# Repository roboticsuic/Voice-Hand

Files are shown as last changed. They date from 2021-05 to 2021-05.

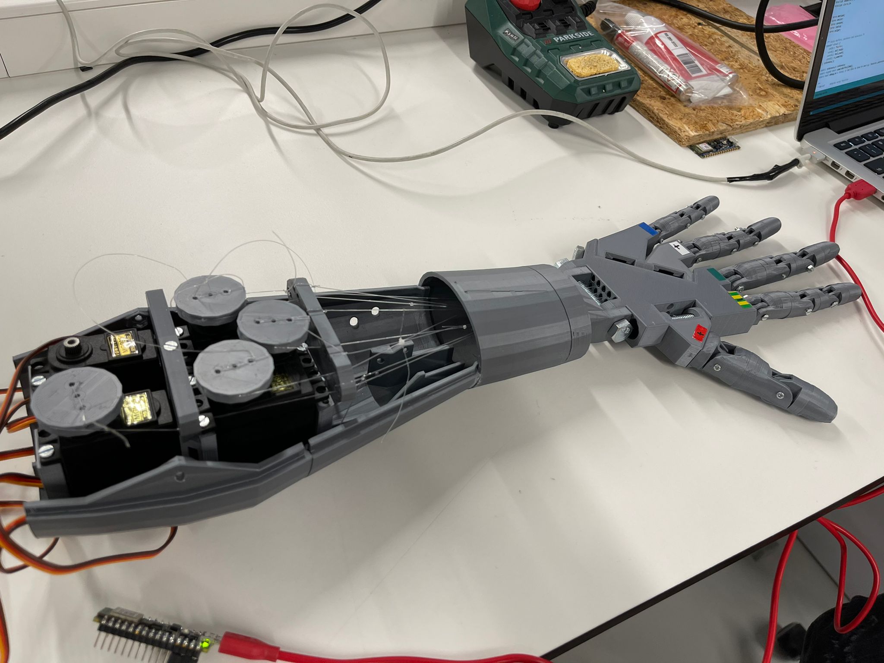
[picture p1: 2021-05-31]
Images and videos/120114522-ced4ec00-c17f-11eb-80c8-0a89fcd72188.jpg

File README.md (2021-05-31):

# Voice-Hand
<h3>A 3D-printed dynamic hand prosthesis with voice recognition software. 
  
Members: Cedric Cordova, Antonio Julia, Saioa Ortiz, and Eduardo Saman
<h2>
INTRODUCTION </h2>
<p>
Do you live with only one hand or ever feel that two just is not enough? The task of biomimicking the human hand, the most dextrous tool ever devised, has taken on new significance and nowadays, owing to new technologies, including 3D printing, it is possible to build your own prosthesis and in a very economical way. 

The project that has been carried out is based on the open-source 3D robotics work called InMoov and the proposed modifications of Patrick S. in its job: “DIY Prosthetic Hand & Forearm (Voice Controlled)”,  which can be found in instructables.com. In this way, this project aims to activate the movement of a prosthetic hand by means of the voice. To do so, it has been used an Arduino Nano 33 BLE Sense system and the software Edge Impulse (which utilizes machine learning and neural networks). The main interest of voice control remains in the fact that muscles are not required.

In relation to the movements that our prosthesis can perform, these can be classified as ROCK (closing all the fingers to form a fist with the hand) or TEST (contracting and relaxing one by one all the fingers). 

Therefore, this report compiles the materials that have been needed, the procedures that have been followed and the problems that have been encountered throughout the challenge, as well as possible improvements that could be made to optimize this prosthesis. Thos projet is based on:https://www.instructables.com/Voice-Controlled-Prosthetic-Hand-Forearm/
	
</p>



<h2> MATERIALS, SOFTWARES, and HARDWARE</h2>
<ul>
<li>Arduino Nano 33 BLE Sense(https://store.arduino.cc/arduino-nano-33-ble-sense)</li>
<li>5x Servo motors MG995(https://es.banggood.com/6X-MG995-High-Torque-Metal-Gear-Analog-Servo-for-RC-Airplane-Models-p-1181877.html?rmmds=detail-left-hotproducts&cur_warehouse=CZ)</li>
Screws:
<li>14 x 2.5mm (or 3mm) bolts (20mm long)</li>
<li>1 x 8mm bolt (55mm long)</li>
<li>1 x 8mm bolt (80mm long)</li>
<li>1 x 8mm bolt (60mm long)</li>
<li>Wires(Macho Macho)</li>
<li>Pins</li>
<li>Fishing line (Nylon)</li>
<li>Breadboard</li>
<li>PRUSA 3D printer</li>
<li>PLA(1.75mm fillament)</li>
<li>Sandpaper</li>
<li>Super glue</li>
<li>Greese</li>
<li>3D Printed(Print each file once)</li>
<li>Ultimaker Cura software</li>
<li>SOLIDWORKS software</li>
<li>Edge Impulse software</li>
</ul>
	
 <h3> Go to the repository for STL files of each part.
</h3>

<h4> 
	APPROXIMATE COST:69€
</h4>


<h2>METHODS</h2>
<p>1. First of all, you need to print out all the parts, which can be found on thingiverse.com. For this, the print setting we used for all the parts were:
</p>
<table>
<thead>
	<tr>
		PRINTING PARAMETERS
	</tr>
</thead>
<tbody>
	<tr>
		<td>Printing Temperature</td>
		<td>Optimal temperature for PLA is 200ºC</td>
	</tr>
	<tr>
		<td>Bed Temperature</td>
		<td>60ºC</td>
	</tr>
  	<tr>
		<td>Speed</td>
		<td>40 mm/s</td>
	</tr>
  	<tr>
		<td>Infill</td>
		<td>20%</td>
	</tr>
  	<tr>
		<td>Support</td>
		<td>None/Change of orientation</td>
	</tr>
</tbody>
</table>

<p>
This parameters may change if the printer used is different, the one we used was PRUSA 

The parts that were printed are the following (you can find them in the zipfile above):</p>
<ul>
	<li>Fingers: Auriculaire3.stl, Index3.stl, Majeure3.stl, ringfinger3.stl, thumb5.stl </li>
	<li> Wrist: robpart1V2.stl,robpart2V3, robpart3V3, WristsmallV3.stl, WristlargeV4.stl</li>
	<li> Half forearm: robpart2V4.stl, robpart3V4.stl, robpart4V3.stl, robpart5V3.stl</li>
	<li>Motor Mounts/Pieces: RobServoBedV5.stl, RobCableFrontV3.stl, RobCableBackV3.stl, RobRingV3.stl</li>
</ul>

<p>2. Once the parts are all printed, we need to start the assembly:

- In order to assemble the joints you will need different types of screws. Maybe it is required to make the holes bigger to facilitate the fit  (you can use a drill, sandpaper or even modify it in solidworks). It is really important to ensure the easy bending of the finger parts, because if not the prosthetic hand will not be able to do all the desired movements and flex without resistance. 
- Take the nylon and pull it through the different parts of the finger (leave enough excess length) and the channels of the hand and wrist. After that, make double knots where the fishing line can slip (tip of the fingers and cable tensioners). The fingers should be able to flex and relax when the strings are tightened (We had to grease the parts where there was the most friction to ensure this smooth movement).
- Some parts will need glue to be attached, but make sure to do it once you have everything else done. Let it dry before using it.

3. As soon as the prosthetic hand and forearm are assembled it is time to start programming. Below, you will find the code we used. 
	</p>


<h2>EDGE IMPULSE</h2>

As we had a problem with the EasyVR board, we had to find a solution for our project and change the initial proposal of using such hardware. We decided to icorporate TiniML by using EDGE IMPULSE vanguard software and platform to keep on with out work. In order to download and stablish connection between the Arduino Nano BLE and the Edge Impulse tools check the configuration in the following link(https://docs.edgeimpulse.com/docs/arduino-nano-33-ble-sense). If there is any problem you can reach out to one of the members of the team using the following email: eduardos@uic.es. This platform work for with Window and macOS users. 

Once connection has been stablished, go to the Edge Impulse webpage(https://www.edgeimpulse.com/) and make sure the arduino board is connected in the 'Devices
' tab. 


Now go to data acquisition and select the microphone from the sensor that the Nano BLE has. 

Record a minimum total of 1 minute for each class andmake each sample lenght of 2 seconds, we included three classes: TEST_DEVICE(saying 'prueba'), ROCK(saying 'cierra'), and noise(background noise to include any other classification that doesn't fall into the previous two on this one). 

<h3>Go to repository to download all the RAW DATA acquired and used for our project</h3>

Use the following blocks to make your processing and create the neural network.

<ul>
<li> Time series data:

	- Window Size: 1000ms for sectioning the raw data into two
	- Window increase: 100ms milliseconds to increase the sliding window for each step
	
</li>
<li> Audio(MFCC)/Feature extracter: a scale used to compare new frequencies with the classified ones(finds features). (source:https://medium.com/prathena/the-dummys-guide-to-mfcc-aceab2450fd)</li>
<li> Neural Network(Keras): the neural network that will process the data and assign weight to the input based on the frequency similarity found in the MFCC features that were found</li>
    </ul>

In the MFCC Block: Use the following parameter to make the feature extraction:
<table>
<thead>
	<tr>
		Parameters
	</tr>
</thead>
<tbody>
	<tr>
		<td>Number of coefficients</td>
		<td>13</td>
	</tr>
	<tr>
		<td>Frame length</td>
		<td>0.02</td>
	</tr>
  	<tr>
		<td>Frame stride</td>
		<td>0.02</td>
	</tr>
  	<tr>
		<td>Filter number</td>
		<td>32</td>
	</tr>
  	<tr>
		<td>Window size</td>
		<td>101</td>
	</tr>
	<tr>
		<td>Low frequency</td>
		<td>300</td>
	</tr>
	<tr>
		<td>Coefficient</td>
		<td>0.8</td>
	</tr>
	<tr>
		<td>Shift</td>
		<td>1</td>
	</tr>
</tbody>
</table>
<p> Then press generate features</p>

<p> It should generate a feature extraction graph like the one below, it shows the features extracted in clusters</p>



<p>Go to the NN CLassifier and add the following parameters and layers to the network. </p>
<table>
<thead>
	<tr>
		Parameters
	</tr>
</thead>
<tbody>
	<tr>
		<td>Number of training cycles</td>
		<td>300</td>
	</tr>
	<tr>
		<td>Learning rate</td>
		<td>0.0001</td>
	</tr>
  	<tr>
		<td>Minimum confidence rating</td>
		<td>0.90</td>
	</tr>
</tbody>
</table>

center

<p> Then start training your network pressing "start training"</p>

<p>it should generate a confusion matrix and tell you the accuracy and loss your algorithm has. Ours shows the following:
	</p>


<p> Once done training, test your model in the 'Live clasification' tab
	
<p> In the 'Deployment' tab, select arduino to create an arduino library that will be exported as a zipfile to be imported by the arduino IDE.</p>
	




<h2> CODE</h2>

<p>
<h3>Go to the repository to download the scripts</h3> There are three scripts, one for the voice_control(generated by the deployment), another for the servo_motors, and one last that integrates both. THe last one didnt work in our presentation, it present an error in the first line which we dont understand why, but added it so you get a general idea on how it would work. Although this happens in the integrated one, the other two work perfectly in separate, so if you want to test it,you have both to give a try to everything. Each script's important features or line are commented with their respective function, purpose and logic behind. </p>

<ul>
	<li>nano_ble33_sense_microphone_ALL: integrated script of how the voice and servo-motors are linked.</li> 
	<li>nano_ble33_sense_microphone_VOICE: only voice, OPEN THE SERIAL MONITOR TO CHECK CLASSIFICATION ONCE IT UPLOADS IT.</li>
	<li>motor_code_only: servo motors</li>
</ul>



<h2> CONCLUSION</h2>
<p>
This project has been carried out as a final work for the Computing, Robotics and Bionics course. All in all, although we have encountered some problems, such as the failure of some of the Servo motors, the Easy VR board (which is used in one of the works from which we have been inspired), the use of softwares that we had never used before, among many others, we have learned a lot and it has been possible to demonstrate that it is feasible to trigger the movement of the fingers of a prosthetic hand by voice alone.

We have been able to explore the different Arduino libraries, how to program with Servos and even how to manipulate various softwares, specifically Edge Impulse. By now, we have mastered analyzing the setbacks as they happen and to find a solution as quickly as possible in order to move forward and overcome them. 

</p>

<h4>DRAWBACKS</h4>
<p>
While  building our robotic hand we confronted a few impediments that we had to overcome. First, one of our servos was faulty ,that is why we can observe in the video that the pinkie finger does not get up. Second, the EasyVR ,where all the voice data and material was, we were not able to make it work with the Arduino as we believe that the board could not process all the information that was inserted. Third, although the hand can partially move the four fingers,once we had all the hand built up and started executing the Arduino code the nylon thread became unstressed and could not realize its function correctly as the threads had to be as tense as possible to arise them completely forward. Another factor that was involved in the lifting of the fingers were the screws and the 3D printed pieces. The failure was due to the rubbing of the material with the screws and with the other piece where it is embedded.
</p>

<h4> FUTURE CONSIDERATIONS</h4>
<p>

As future improvements, we believe that changing the measurements of the pieces with Solidworks and using a through screw instead of a threaded screw would decrease the friction and permit the piece to move more freely, leaving the fingers to complete the entire movement. On the other hand, we also consider substituting  the nylon threads for another type of material that would not yield. And last, for the EasyVR we speculate that replacing the board for another one with more load capacity the system might not collapse and it could work.
</p>

<h4>EXTRA RESOURCES</h4>
<h5>Video</h5>

https://user-images.githubusercontent.com/60470010/120114667-88cc5800-c180-11eb-960b-8f8175e6065a.mov

https://user-images.githubusercontent.com/60470010/120114514-c977a180-c17f-11eb-8ab9-50ce27240681.mp4
	
https://user-images.githubusercontent.com/60470010/120162486-bb199c00-c1f8-11eb-9495-e3a71cc8e68f.mov

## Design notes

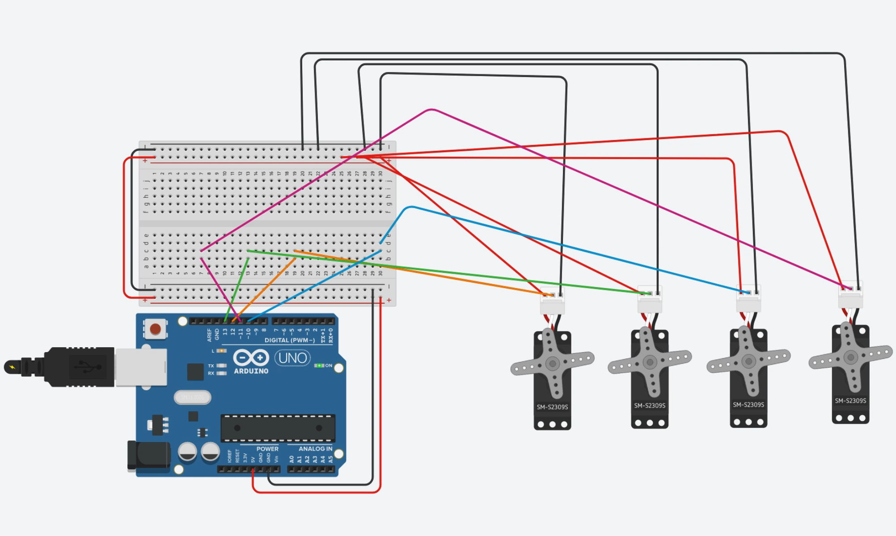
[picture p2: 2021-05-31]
Images and videos/Screen Shot 2021-05-31 at 11.46.51 AM.png

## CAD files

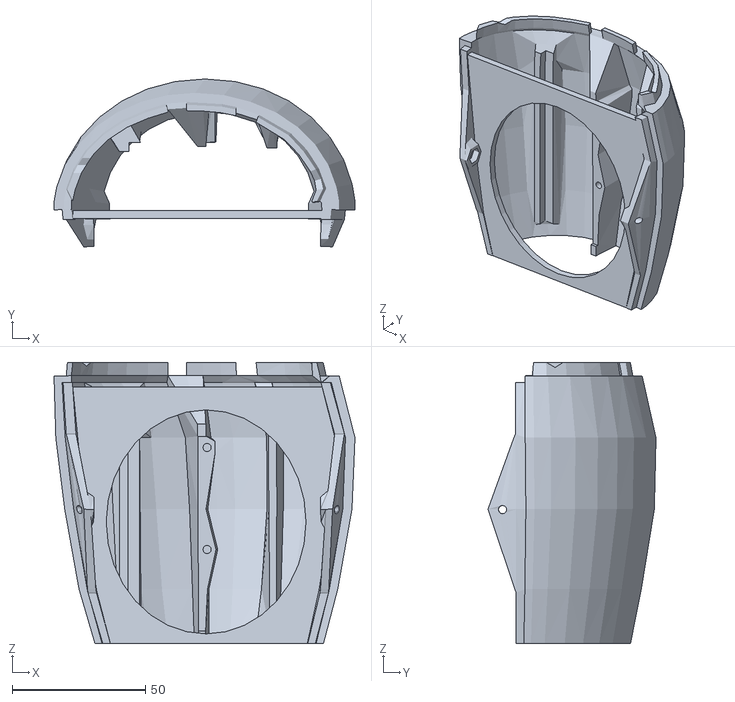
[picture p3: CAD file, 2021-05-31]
STL Files/ARM/robpart5V3.stl
113.0 x 63.1 x 105.7

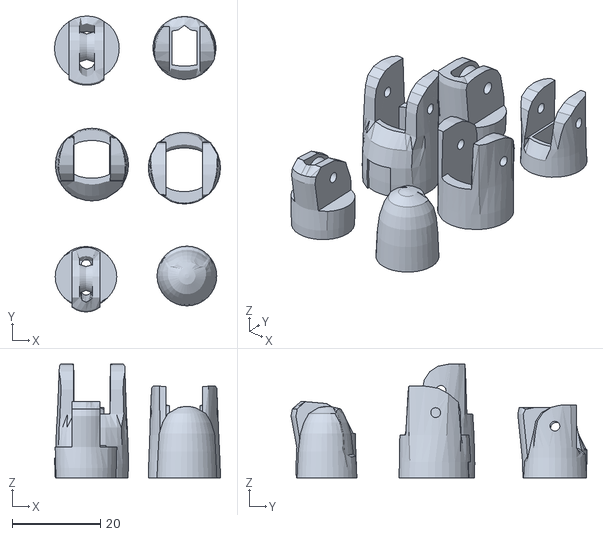
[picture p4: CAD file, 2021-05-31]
STL Files/FINGERS/ringfinger3.stl
37.6 x 67.0 x 25.8

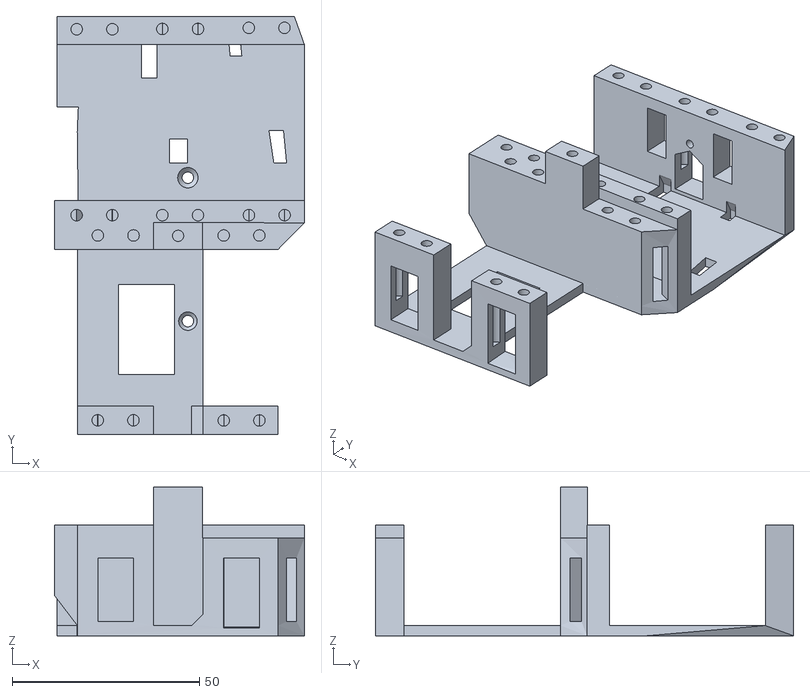
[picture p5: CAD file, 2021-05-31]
STL Files/SUPPORT-RINGS/RobServoBedV5.stl
66.7 x 111.6 x 39.7

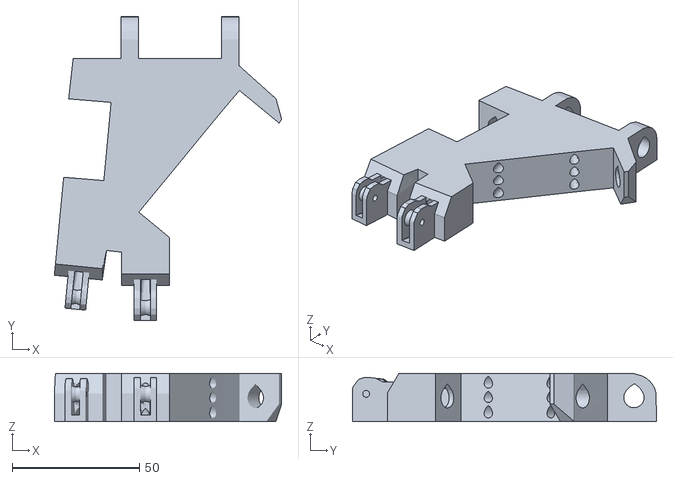
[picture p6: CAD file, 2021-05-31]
STL Files/WRIST/WristlargeV4.stl
89.2 x 119.4 x 18.9

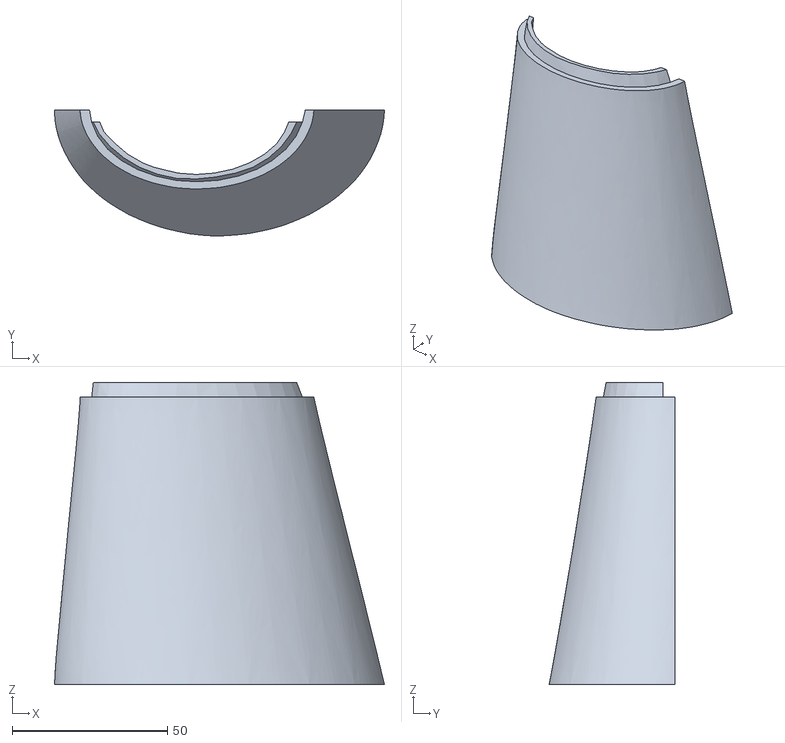
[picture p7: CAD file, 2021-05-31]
STL Files/ARM/robpart3V4.stl
106.4 x 40.6 x 97.5

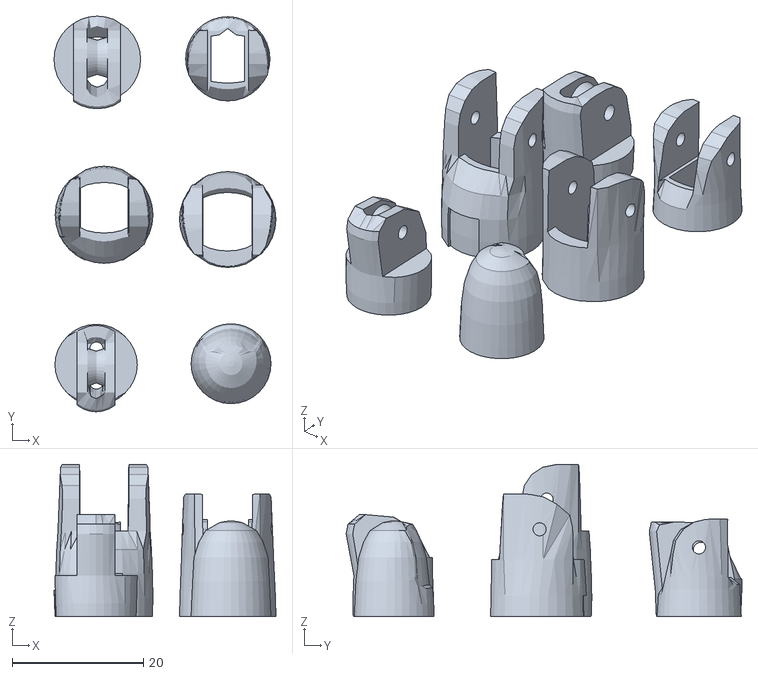
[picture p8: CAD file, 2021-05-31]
STL Files/FINGERS/Auriculaire3.stl
33.8 x 60.3 x 23.2

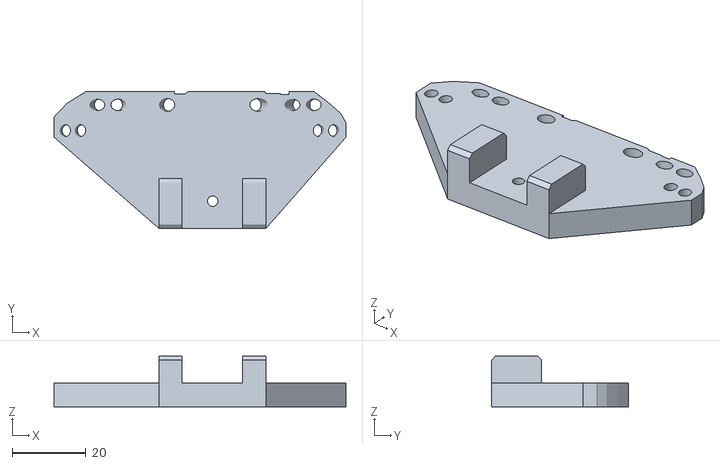
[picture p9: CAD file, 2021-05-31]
STL Files/SUPPORT-RINGS/RobCableFrontV3.stl
79.3 x 37.1 x 13.8

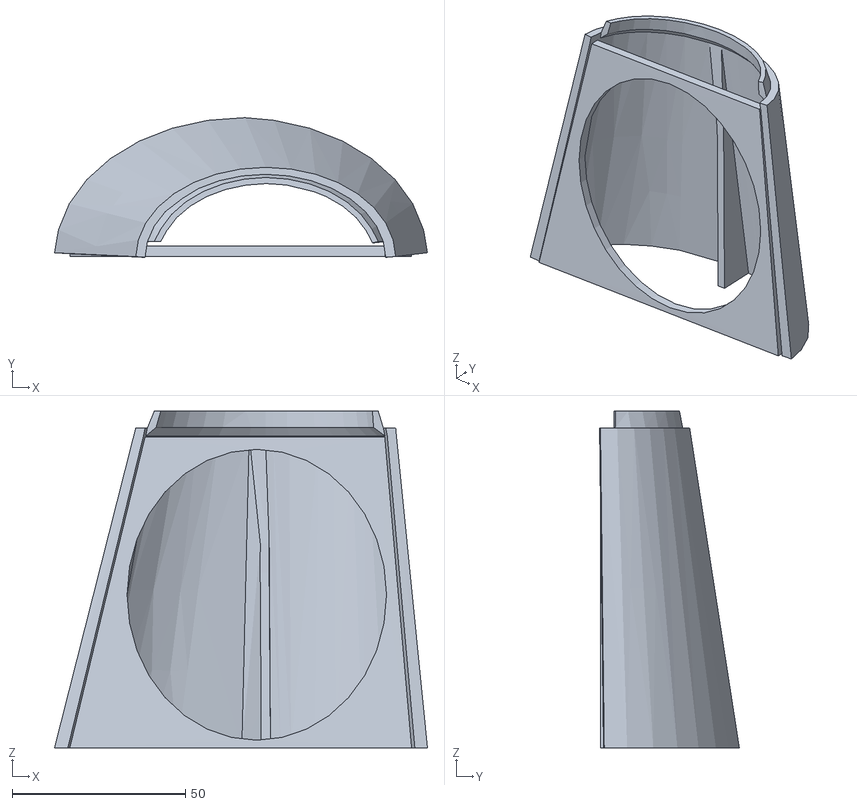
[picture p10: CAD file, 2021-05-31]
STL Files/WRIST/robpart3V3.stl
107.8 x 40.4 x 97.3

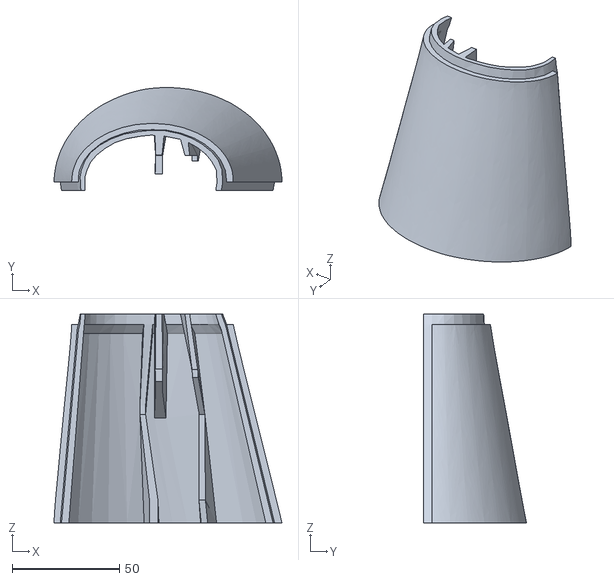
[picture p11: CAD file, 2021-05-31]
STL Files/ARM/robpart2V4.stl
106.4 x 48.1 x 97.5

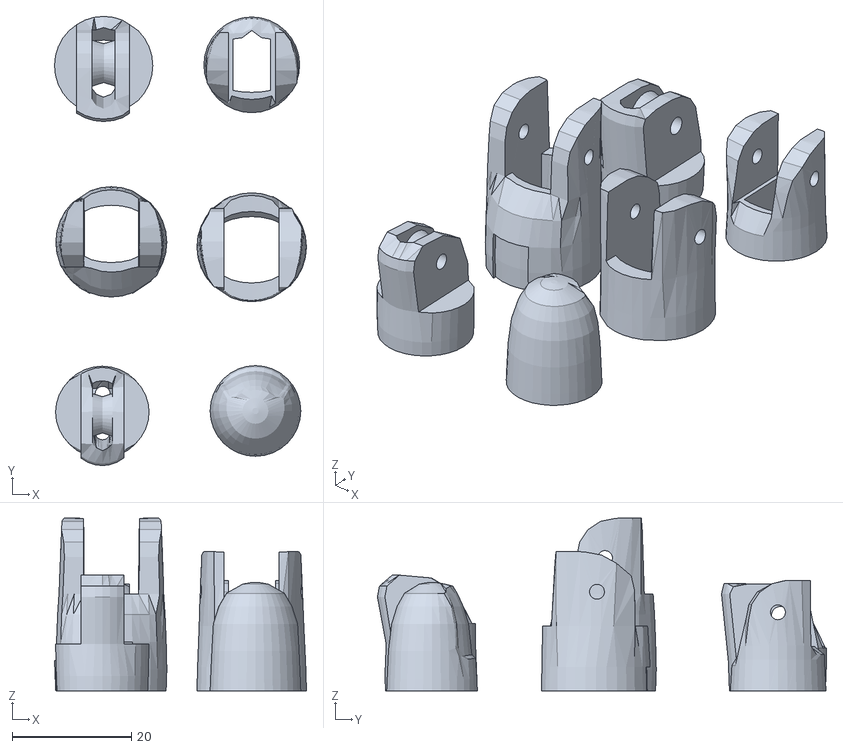
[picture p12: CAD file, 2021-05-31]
STL Files/FINGERS/Majeure3.stl
42.2 x 75.2 x 29.0

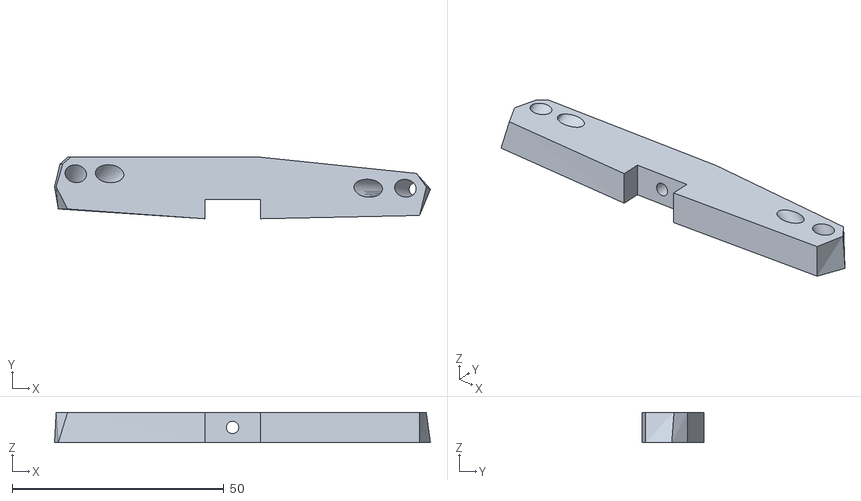
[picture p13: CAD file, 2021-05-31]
STL Files/SUPPORT-RINGS/RobCableBackV3.stl
88.7 x 14.5 x 7.17

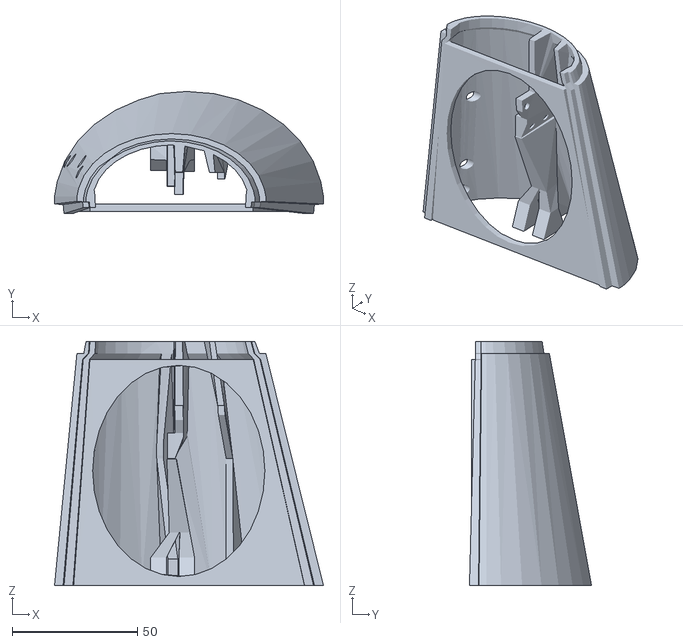
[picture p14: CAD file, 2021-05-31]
STL Files/WRIST/robpart2V3.stl
107.2 x 48.7 x 97.3

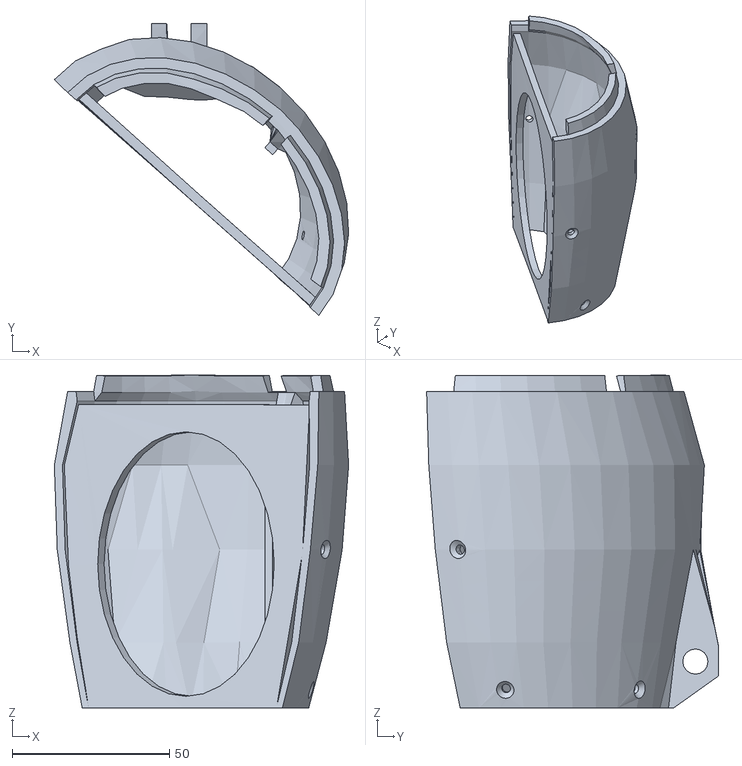
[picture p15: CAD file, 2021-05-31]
STL Files/ARM/robpart4V3.stl
93.5 x 92.7 x 105.8

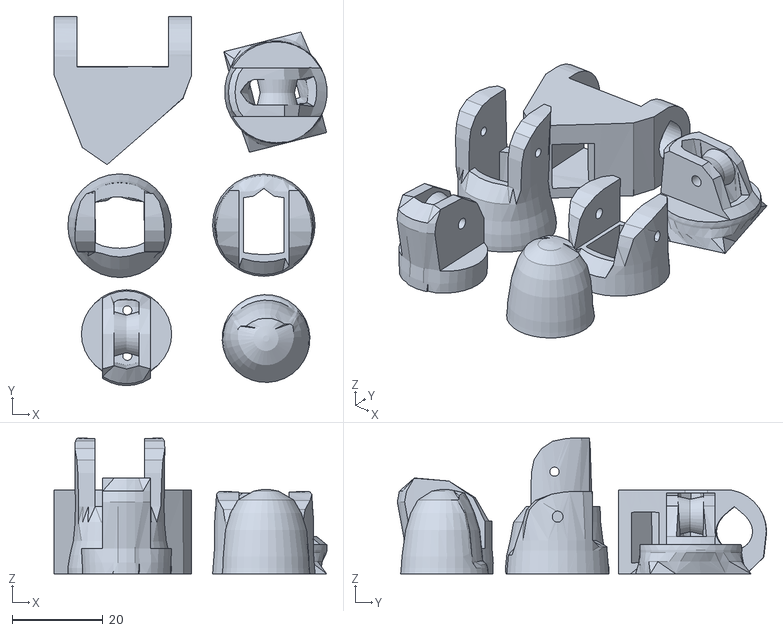
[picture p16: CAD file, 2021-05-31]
STL Files/FINGERS/thumb5.stl
60.1 x 81.2 x 29.8

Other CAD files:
STL Files/SUPPORT-RINGS/RobRingV3.stl
STL Files/WRIST/robpart1V2.stl
STL Files/FINGERS/Index3.stl
STL Files/WRIST/WristsmallV3.stl
